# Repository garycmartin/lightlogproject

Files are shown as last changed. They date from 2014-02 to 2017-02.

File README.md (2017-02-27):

Lightlog Project
===============

A wearable, Open Source, ambient colour light tracker.

Installation
------------

To download data from Lightlog you'll need to set up your machine with some standard tools.

1) Install the device driver for the USB sync cable, install documentation steps, and driver are available at:

<http://www.picaxe.com/Software/Drivers/AXE027-USB-Cable-Driver/#download>

2) For Mac and Linux systems Python is usually already installed. If your using Windows and don’t have Python installed, there's a nice quick guide here if you need it. Please note that the scripts current require Python 2.7:

<http://www.anthonydebarros.com/2011/10/15/setting-up-python-in-windows-7/>

3) For Windows, make sure Python is added to your PATH variable, this is covered in the above guide.

```
C:\Python27;C:\Python27\Lib\site-packages\;C:\Python27\Scripts\;
```

4) Install pySerial module. The above guide also includes steps to add setuptools and pip, once you have them added you can type:

```shell
pip install pyserial
```

5) Download the lightlogdownload.py script from:

<https://raw.githubusercontent.com/garycmartin/lightlogproject/master/python/lightlogdownload.py>

…or make a local clone of the git repository. Github provides graphical git clients at <https://desktop.github.com> if needed.

6) Test that you can run the script ok by trying to use the command console or a shell window to check the script version:

```shell
python lightlogdownload.py --version
Version v0.13
```

7) Finally, plug in the serial cable, attach a Lightlog, and run the script...

Basic workflow
--------------

The usual work flow is to run:

```shell
python lightlogdownload.py --both
```

This will try to automatically find the connected serial port and communicate with Lightlog. Hold the button down on the Lightlog when it asks to establish the down link. The script will then download all logged data and save a .csv file of lux values containing red, green, blue, white, epoch seconds, and flags. The auto save file name includes the Light Log's unique ID, and if the save file already exists it will append any new data since the last download. This should make it easy to plug in each device, one after the other, and run the command each week to build up a continuous archive of data. Make sure you grab the data once a week (the default is one record a minute) or you'll have gaps in your data (at one record a minute, the memory holds 7days 14hrs worth of samples).

The epoch timestamps are seconds since 1st, Jan, 1970 (AKA Unix time, or POSIX time), you can quickly check a timestamp if needed with the below code snipped:

```shell
python -c 'import datetime; print (datetime.datetime(1970,1,1) + datetime.timedelta(seconds=1395802371))'
2014-03-26 02:52:51
```

For reference here's the download command's full arguments:

```
$ python lightlogdownload.py --help
usage: lightlogdownload.py [-h] [-p PORT] [-r] [-b] [--csv-header]
                           [--estimate]
                           [-f FILE | --stdout | --cal {2.5k,5k,10k} | --delay DELAY |
                           --phase PHASE | --sample SAMPLE | --status | --reset-memory |
                           --reset-cal | --reset-goal | --factory-reset | -v]
    
Download, convert and save data from Lightlog device. Without arguments data will be
saved to an auto-named csv file Light_Log_<device_ID>.csv in the current directory, if
the log file already exists, new data will be appended to the log.

optional arguments:
   -h, --help            show this help message and exit
   -p PORT, --port PORT  serial or COM port name
   -r, --raw             raw 10-bit sensor data, no conversion to lux scale
   -b, --both            auto saves two files, raw 10-bit sensor data and one
                         in lux
   --csv-header          outputs column header in first row of data (new log
                         files only)
   --estimate            force time estimate based on device period setting
                         rather than log time data
   -f FILE, --file FILE  save downloaded data to a named file
   --stdout              send data to console sandard output
   --cal {2.5k,5k,10k}   calibrate hardware to current lux light exposure
   --delay DELAY         fine tune device delay timing between samples 500-2000
                         (default 1000 = 10sec)
   --phase PHASE         set day phase 0-1439 in min (used for resetting daily
                         goal)
   --sample SAMPLE       number of samples per average 1-63 (default is 6
                         giving 1 record every minute)
   --status, -s          display device status data
   --reset-memory        reset memory pointer (for a fresh logging session)
   --reset-cal           reset lux calibration back to factory defaults
   --reset-goal          reset daily light goal
   --factory-reset       reset device back to all factory defaults, new unique
                         hardware ID will be generated (!!!)
   -v, --version         show download software version number and exit
```

Lightlogdownload.py script
--------------------------

When synching your devices I recommend using either the --raw or --both option, these generate a copy of the raw data before any calibration is applied (each device will generate a Light_Log_<device_ID>_raw.csv). If needed, this then allows you to control lux conversion/calibration using your own protocol, test equipment and math functions.

Without --raw or --both, you will only have the record of data after lux conversion has been applied using the code in Lightlogdownload.py. I have experimented with a number of fitted math curves to sample data sets, but none of them were satisfactory. My closest fit has been simply by interpolating between a set of lux vs. calibration data. The code is currently linearly interpolating between 16 calibration points.

Colour data
-----------

This python definition can be used if you want to convert the RGB values to colour temperature estimates:

```python
def calculate_colour_temp(colour):
   r = colour[0]
   g = colour[1]
   b = colour[2]
   n = ((0.23881 * r) + (0.25499 * g) + (-0.58291 * b)) / ((0.11109 * r) + (-0.85406 * g) + (0.52289 * b))
   cct = int(round(449 *  n ** 3 + 3525 *  n ** 2 + 6823.3 * n + 5520.33))
   return cct
```

Here’s another better commented example from Adafruit, where they use a library for the same sensor for Raspberry PI <https://github.com/adafruit/Adafruit-Raspberry-Pi-Python-Code/blob/master/Adafruit_TCS34725/Adafruit_TCS34725.py>

```python
def calculate_colour_temp2(colour):
   r = colour[0]
   g = colour[1]
   b = colour[2]

   # 1. Map RGB values to their XYZ counterparts.
   # Based on 6500K fluorescent, 3000K fluorescent
   # and 60W incandescent values for a wide range.
   X = (-0.14282 * r) + (1.54924 * g) + (-0.95641 * b)
   Y = (-0.32466 * r) + (1.57837 * g) + (-0.73191 * b) # also lux?
   Z = (-0.68202 * r) + (0.77073 * g) + ( 0.56332 * b)
    
   #2. Calculate the chromaticity co-ordinates
   xc = (X) / (X + Y + Z)
   yc = (Y) / (X + Y + Z)
    
   #3. Use McCamy's formula to determine the CCT
   n = (xc - 0.3320) / (0.1858 - yc)
    
   #Calculate the final CCT
   cct = (449.0 * n**3) + (3525.0 * n**2) + (6823.3 * n) + 5520.33
   return cct
```

For the raw data R, G, B, W, Time, Flag; R, G, B are 10-bit (0-1023) % of W, and W is a 10-bit exponential stored value of the original sensor reading (based on potentially two different 16-bit sensor gain exposures, depending on light brightness, see below).

The cases where you see W > R+G+B will be down to the 10-bit resolution the data is stored to memory. The sensor device samples 16-bit data, and may take two exposures of light (if needed) at different gains, one at x16, if that over exposes it then takes a second sample at x1 gain. It then takes the 16-bit W value and uses it to create a delta value for each R, G, B from W. W is then converted to 10-bits of data using a logarithmic scale so there is high detail for indoor lighting environments, but outdoor cases are still covered. R, G, B are then each converted to 10-bit (0-1023) % values of the W value (e.g. if the red sensor was 50% of the white sensor, R=511), this provides maximum resolution for R, G, B for both high values of W and low values of W.
 
The FIFO log buffer, with the default delay of one RGBW+flag record per minute, will last 7.5 days before data starts being ovberwritten. For the most accurate of log file timing it is best that some of your data overlaps your previous log, if found, lightlogdownload.py will use this data overlap to adjust sample deltas using the accurate system clock. If the data does not overlap lightlogdownload.py uses the devices sample rate to set a fixed time between records (most recent records will be the most accurate, with oldest records having most drift).
 
There are 64Kbytes available on the EEPROM for logging, each record is 6 bytes, giving 10922 available records 

You'll occasionally see something like this from lightlogdownload.py:

```
 Device day phase was 225min, now set to 227min
 Device delay tuning is set to 982 (984 suggested)
 ```
 
The first item refers to the day phase (1440min each day, local midnight=0min). The second appears if there was a reasonable number of new samples, it tells you the current timing delay used by this device, and its suggestion. You can see here it suggesting the device slows down a little to correct for the time drift. If you agree you can run:

```shell
$ python lightlogdownload.py --delay 984
```

It's not done automatically during a sync as it can't know how long you might have removed a battery for while replacing/changing. The delay value is already tuned at least a couple of times for the devices logging test data (over a couple of days duration minimum). Note that if your previous log file data overlaps with data in the device, lightlogdownload.py will adjust the sample timings between the start and end records using the real system time from your computer.

Battery life
------------

Expect 4 months (+/- a week) between battery changes under normal conditions. Be aware that very low temperatures will lower the battery voltage output.

If you want to have a safe margin of error, swap a battery once the script reports below 2.1V, you'll probably also notice the LEDs start to dim around this time as well.

The serial sync process and LED display are the most power hungry spikes that dip the voltage, so if the battery is low you may get a failed or no response message when trying to sync. Swapping out the battery for a new one, and trying to sync again should get all the data downloaded just fine.

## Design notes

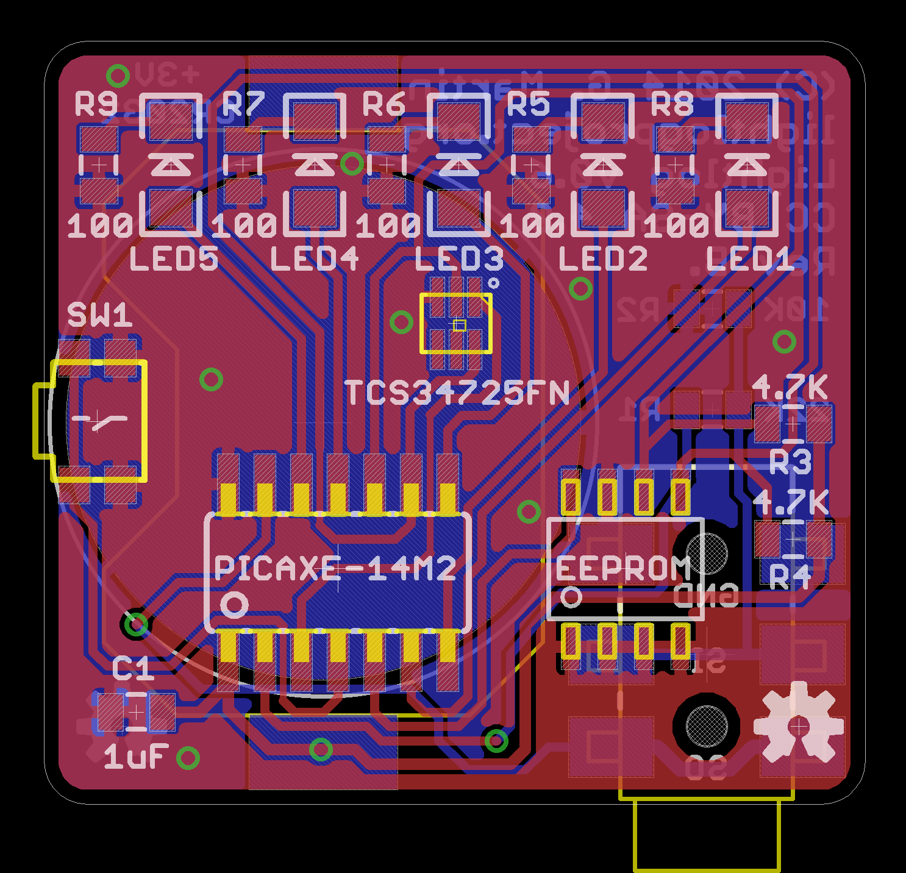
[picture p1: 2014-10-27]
circuit_design/LightLog_SMD_0.6B_BRD.png

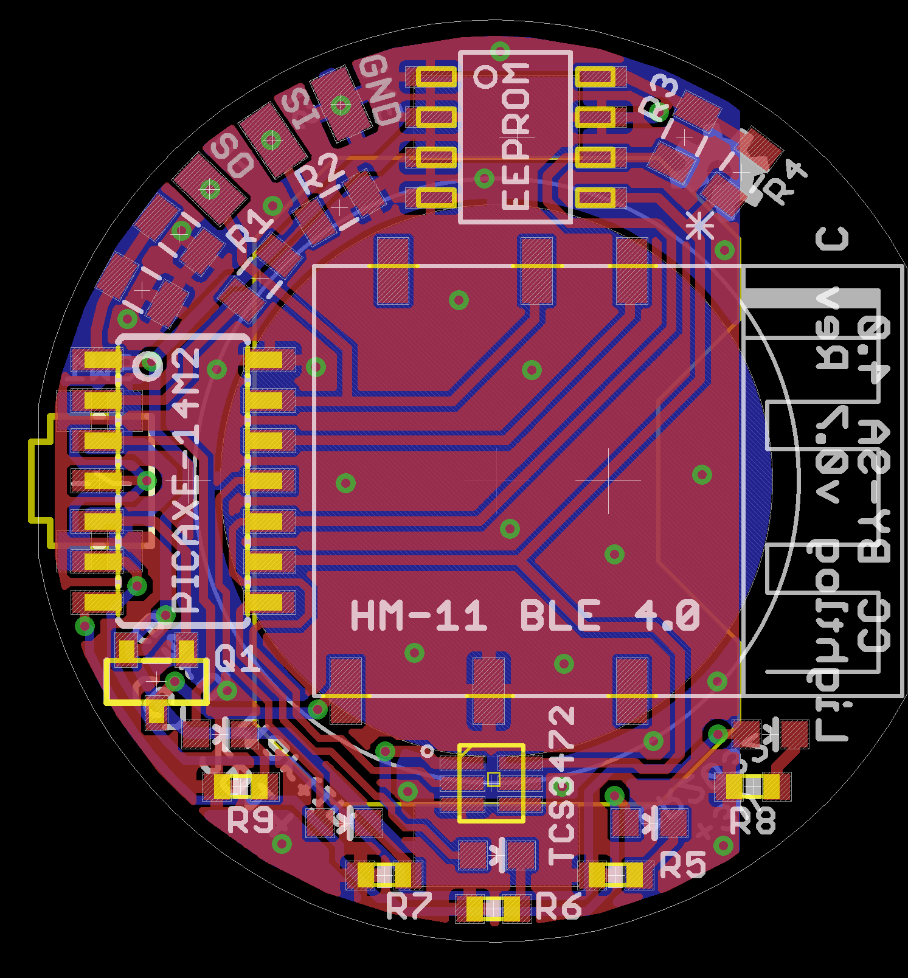
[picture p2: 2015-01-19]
circuit_design/LightLog_SMD_0.7_REV_C.png

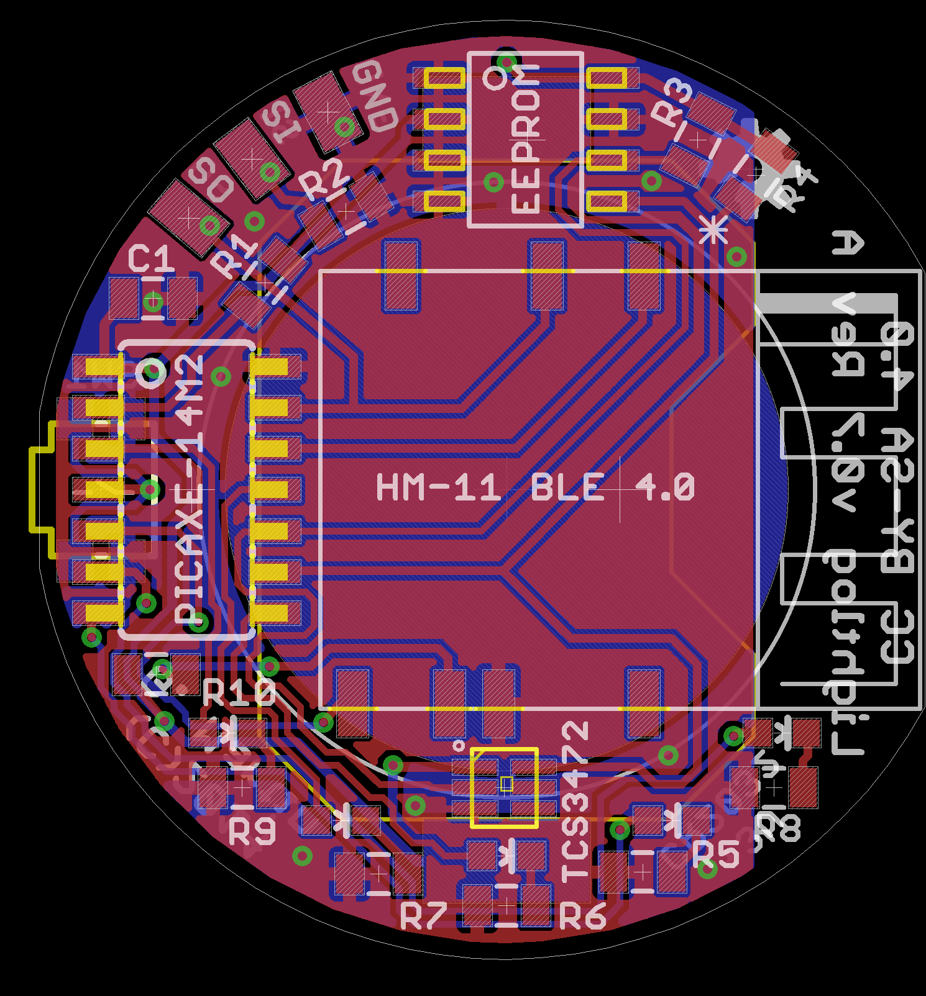
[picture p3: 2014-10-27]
circuit_design/LightLog_SMD_0.7_Rev_A.png

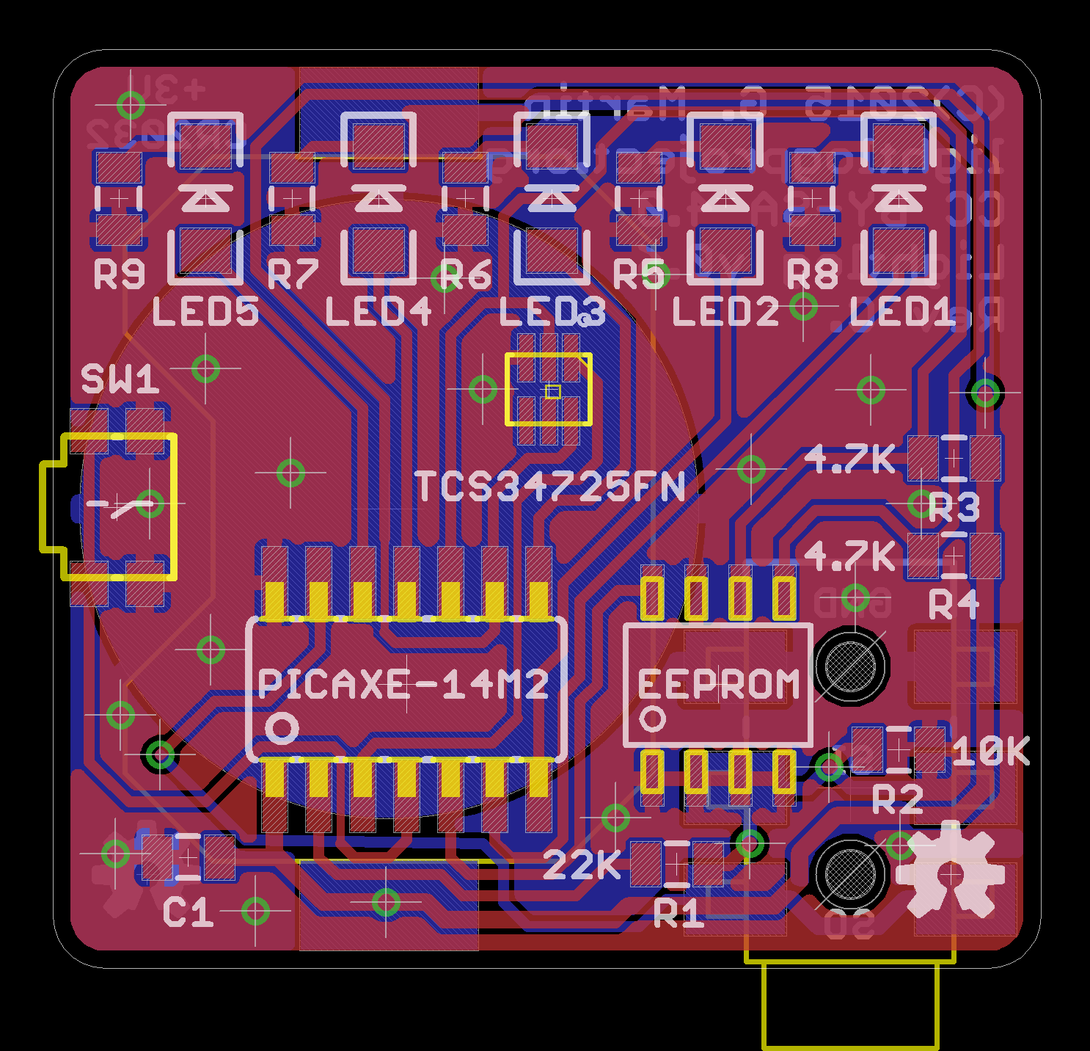
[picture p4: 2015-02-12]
circuit_design/LightLog_SMD_0.6_REV_C.png

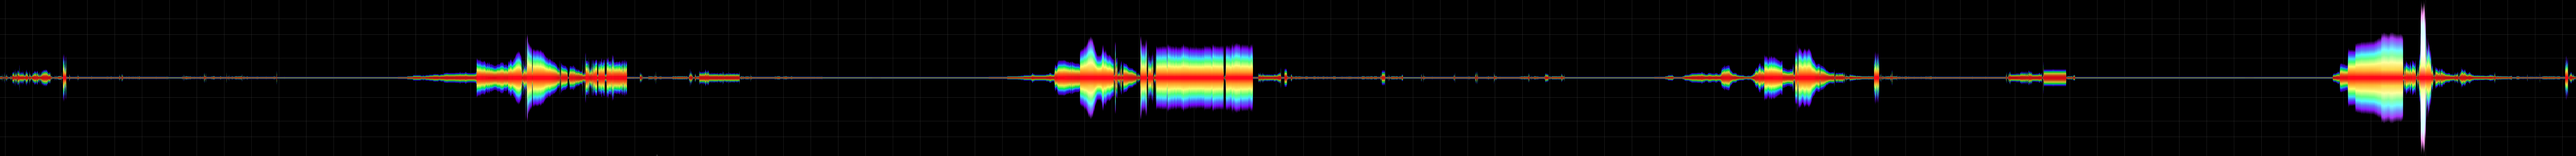
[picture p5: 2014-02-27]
data_log_samples/light_log_sample_data_2014-01-11-18-40-23_to_2014-01-15-20-29-13.png

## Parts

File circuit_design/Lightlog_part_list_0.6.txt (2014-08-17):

=== Light Log SMD/SMT prototype v0.6 part list ===

Surface Mount PICAXE-14M2 [AXE017M2SM]
24AA512-I/SN 64Kb Microchip EEPROM SMT slim SOIC-8 3.9mm width package (with extra low 1.7V drop-out)
TCS34725FN ams RGBC Light to Digital Converters (with IR filter)
C1. 100nF decoupling capacitor Y5V0805CTTE105Z Ceramic Capacitors MLCC - SMD/SMT
LED1, LED2, LED3, LED4, LED5 white VAOL-S12WR4 Standard LED - SMD
SMT Battery Holder BAT-HLD-001 Linx CR2032
R1 22Kohm SG73S2ATTD2202F KOA Speer Thick Film Resistors SMD (limit current to serial in)
R2 10Kohm SG73P2ATTD1002F KOA Speer Thick Film Resistors SMD (stops serial in from floating)
R3, R4 4.7Kohm SG73S2ATTD4701F KOA Speer Thick Film Resistors SMD (pull-ups for I2C)
R5, R6, R7, R8, R9 50ohm-100ohm SG73P2ATTD1000F KOA Speer Thick Film Resistors SMD (LED current limit)
SW1 Tactile side button SW04440 MICROSWITCH, MINIATURE; Actuation Type:S KMS231G LFS, C&K COMPONENTS
3.5mm stereo socket MJ4435-R SMD/SMT [CON039SM]
USB to 3.5mm jack FTDI based serial cable [AXE027] (for Pic serial programming and data sync)
CR2032 Coin cell battery 3V (circuit operating range 2.1V-5.5V, 240mAh will last >4 months)

Where given, part numbers [in square brackets] can be found at techsupplies.co.uk. Many parts can also be found at other suppliers such as mouser.com, cpc.farnell.com and farnell.com. This prototype requires a custom 2 layer PCB board, LightLog_SMD_0.6_BRD, for assembly due to small SMD/SMT components.

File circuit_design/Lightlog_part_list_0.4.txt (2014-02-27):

=== Light Log prototype v0.4 part list ===

PICAXE-14M2 [AXE017M2] (also available as a SMD component)
24LC512 64K EPROM [MIC051] (also available as a SMD component)
3 x Miniature LDR [SEN002] (~2Mohm dark current)
Red filter light gel (coloured acetate or cellophane will also work adequately)
Green filter light gel (coloured acetate or cellophane will also work adequately)
Blue filter light gel (coloured acetate or cellophane will also work adequately)
R3, R4, R5, R6, R7. 5 x 4.7Kohm resistors
C1. 100nF polyester decoupling capacitor (not strictly needed but recommended)
R8. 50ohm to 100ohm resistor (current limit for LED, can be omitted @ 3V or less operation)
LED (Example, diffused white 3mm LED 3.0-3.4V Forward Voltage, at 20mA from Adafruit)

USB to 3.5mm jack FTDI based serial cable [AXE027] (for Pic serial programming and light data sync)
3.5mm stereo socket [CON039] (or [CON039SM] for surface mount version)
R2. 10Kohm resistor to stop serial in from floating when disconnected from computer (essential for Pic operation)
R1. 22Kohm resistor to limit current in from computer to serial in

CR2032 Coin cell 3V (circuit will operate between 2.1V and 5.5V)
CR2032 battery holder (Example, [BAT004H] worked well dring breadboard prototyping)

Where given, part numbers (in square brackets) can be found at http://www.techsupplies.co.uk though many of these parts can be found at other suppliers.

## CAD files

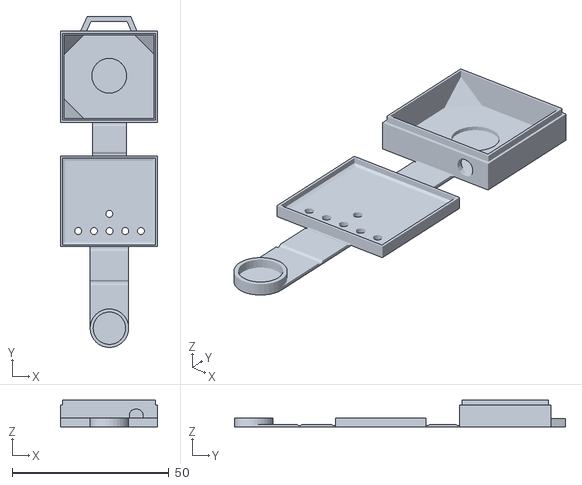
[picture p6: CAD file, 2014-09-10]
case_enclosures/LightLog_3d_enclosure.stl
30.8 x 105.5 x 8.55

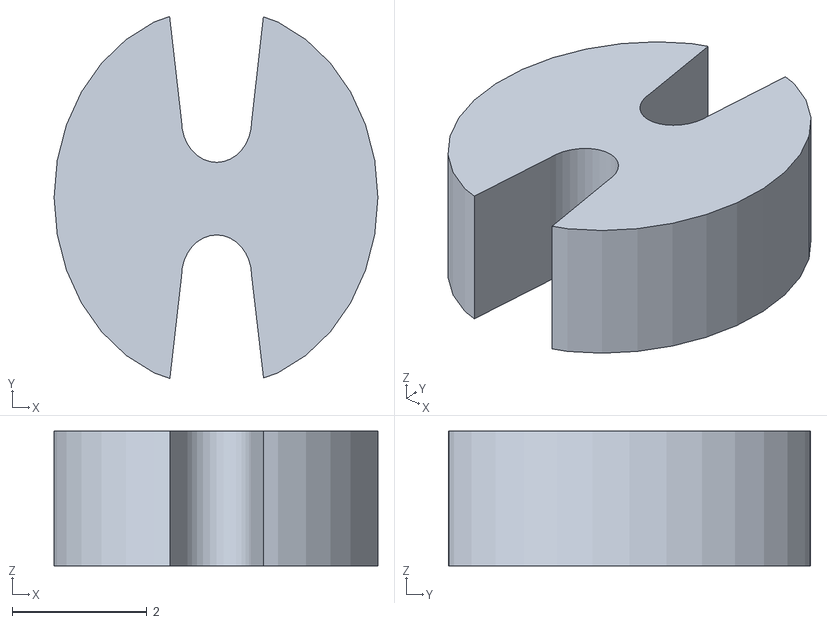
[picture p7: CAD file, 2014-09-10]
case_enclosures/LDR_spacer.stl
4.80 x 5.37 x 2.00

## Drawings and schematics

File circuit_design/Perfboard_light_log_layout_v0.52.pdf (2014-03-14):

Bottom copper view of main perfboard (v0.52) | Bottom copper view of power/comms perfboard (v0.52)

# Light Log Project (v0.52)

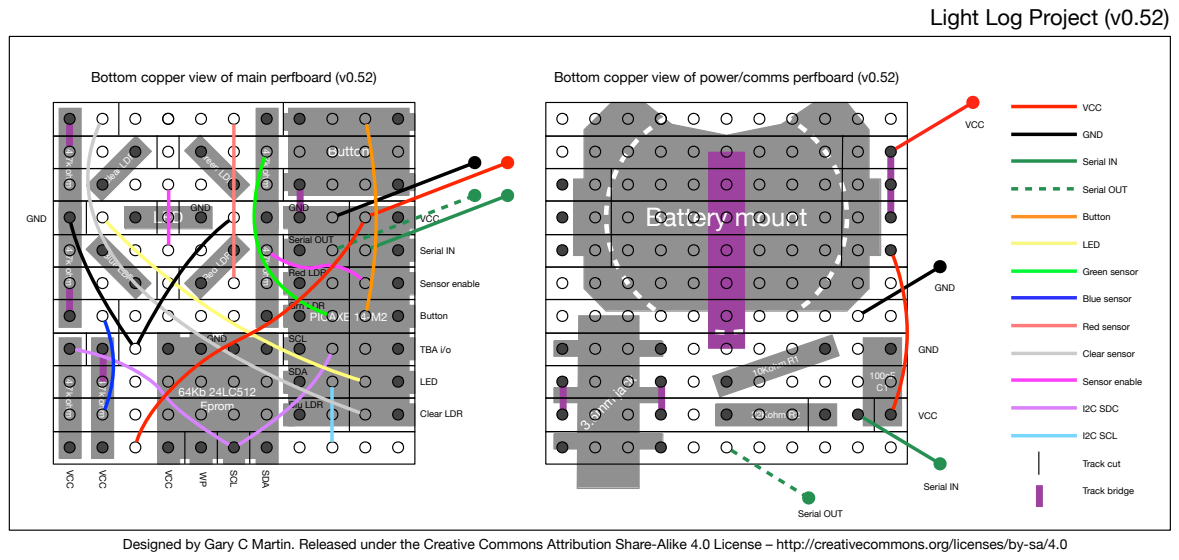
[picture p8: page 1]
PICAXE 14-M2; Button; 64Kb 24LC512 Eprom; 4.7k ohm; LED; Clear LDR; Red LDR; Green LDR; Blue LDR; 4.7k ohm 4.7k ohm; 3.5mm jack; 22Kohm R2; 10Kohm R1; Battery mount; TBA i/o; VCC; Serial IN; Sensor enable; SCL; SDA; GND; Serial OUT; Grn LDR; Blu LDR; Green sensor; Blue sensor; Red sensor; I2C SDC; I2C SCL; Clear sensor; Track cut; Track bridge

Designed by Gary C Martin. Released under the Creative Commons Attribution Share-Alike 4.0 License – http://creativecommons.org/licenses/by-sa/4.0

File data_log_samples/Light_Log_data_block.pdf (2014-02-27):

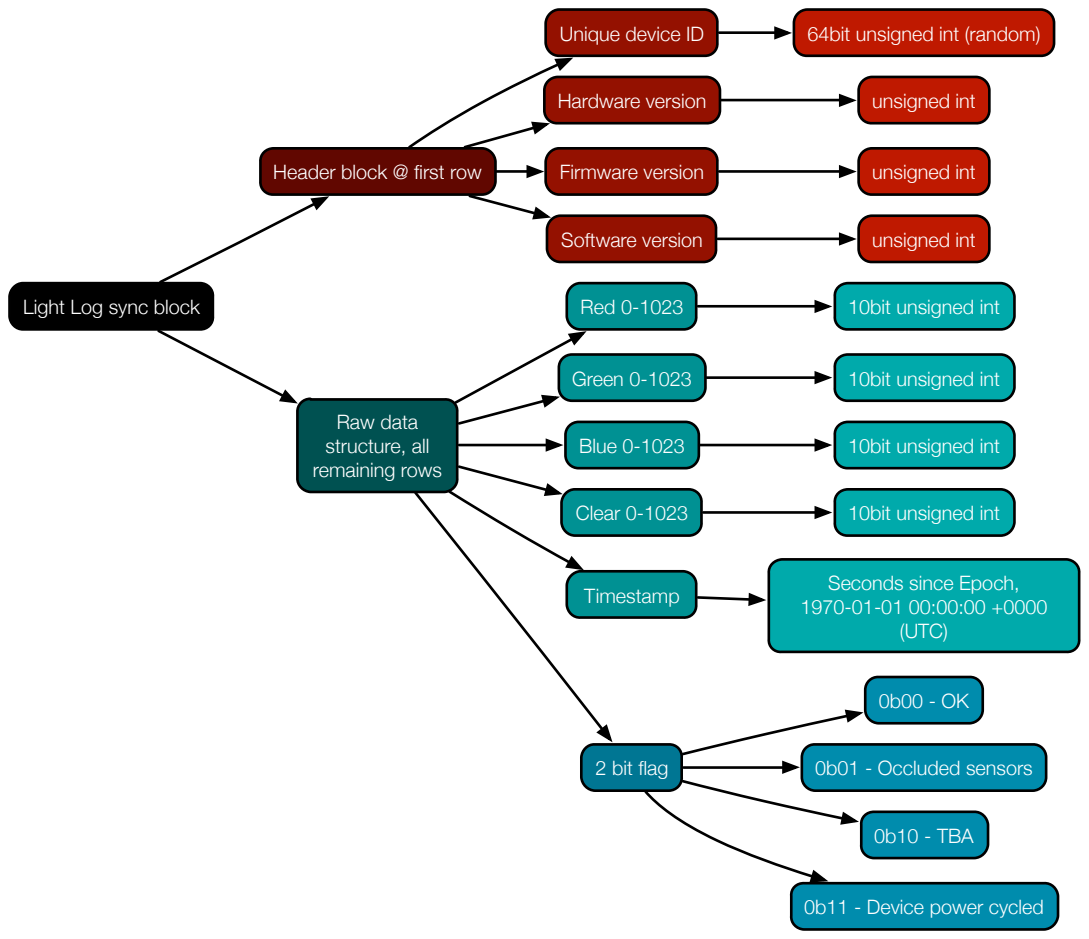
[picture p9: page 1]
Unique device ID; 64bit unsigned int (random); Hardware version; unsigned int; Firmware version; Software version; Raw data structure, all remaining rows; Red 0-1023; 10bit unsigned int; Green 0-1023; Blue 0-1023; Clear 0-1023; Timestamp; Seconds since Epoch,; 1970-01-01 00:00:00 +0000 (UTC); 2 bit flag; 0b01 - Occluded sensors; 0b10 - TBA

Header block @ first row

Light Log sync block

0b11 - Device power cycled

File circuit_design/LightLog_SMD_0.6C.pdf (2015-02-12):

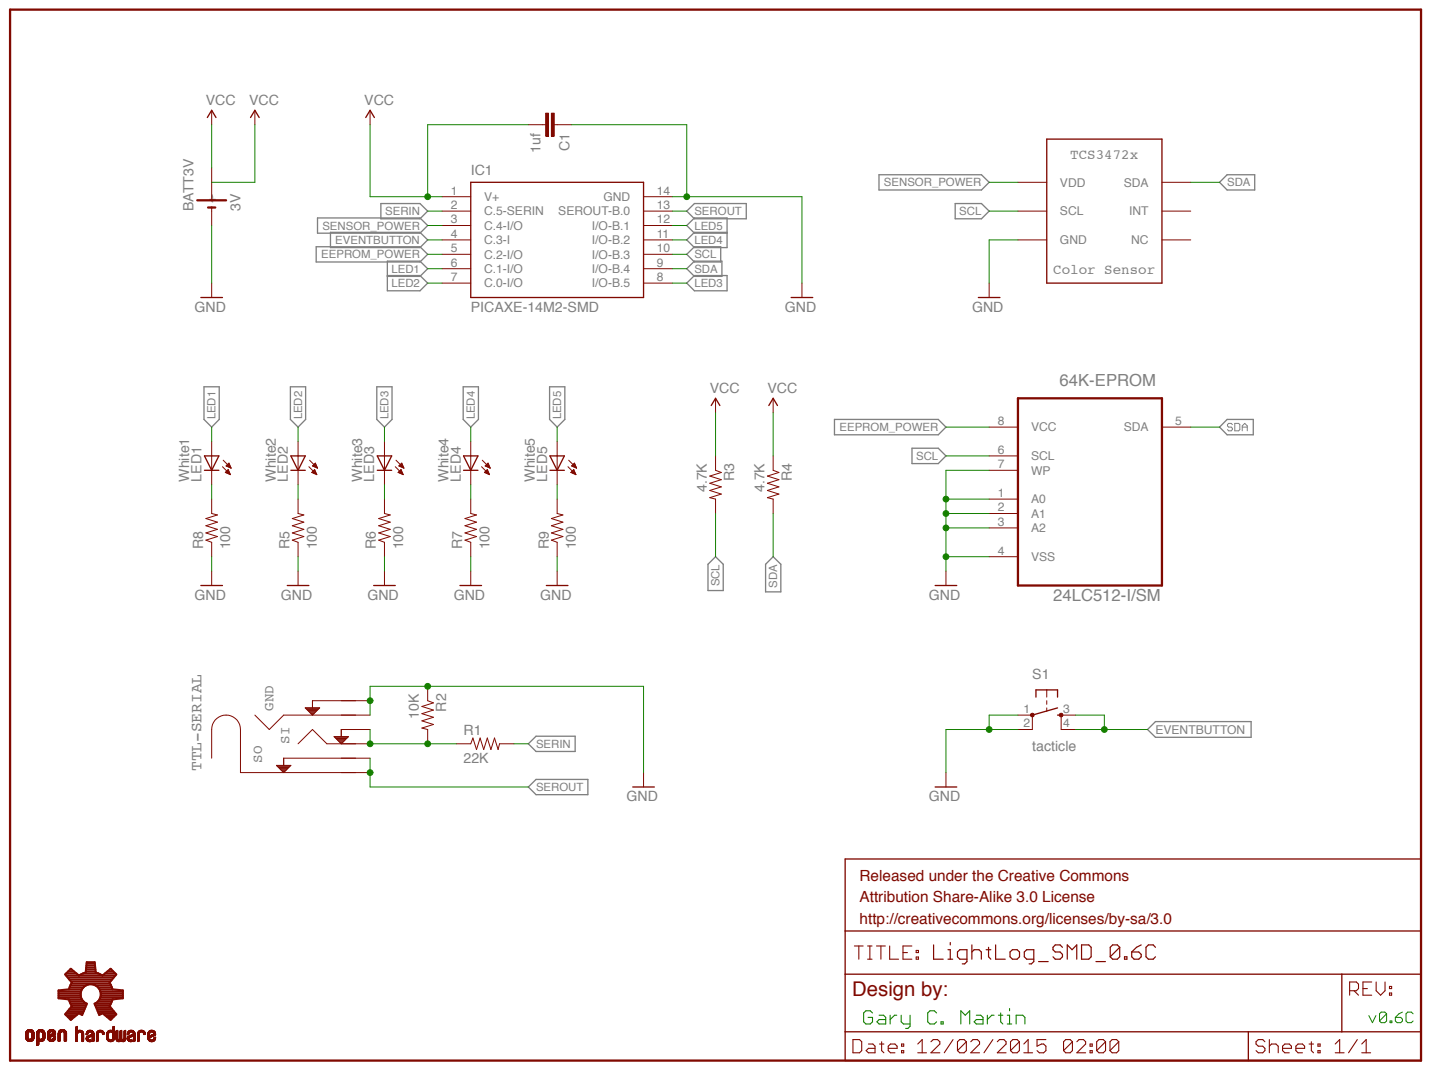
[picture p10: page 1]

Released under the Creative Commons
Attribution Share-Alike 3.0 License
http://creativecommons.org/licenses/by-sa/3.0

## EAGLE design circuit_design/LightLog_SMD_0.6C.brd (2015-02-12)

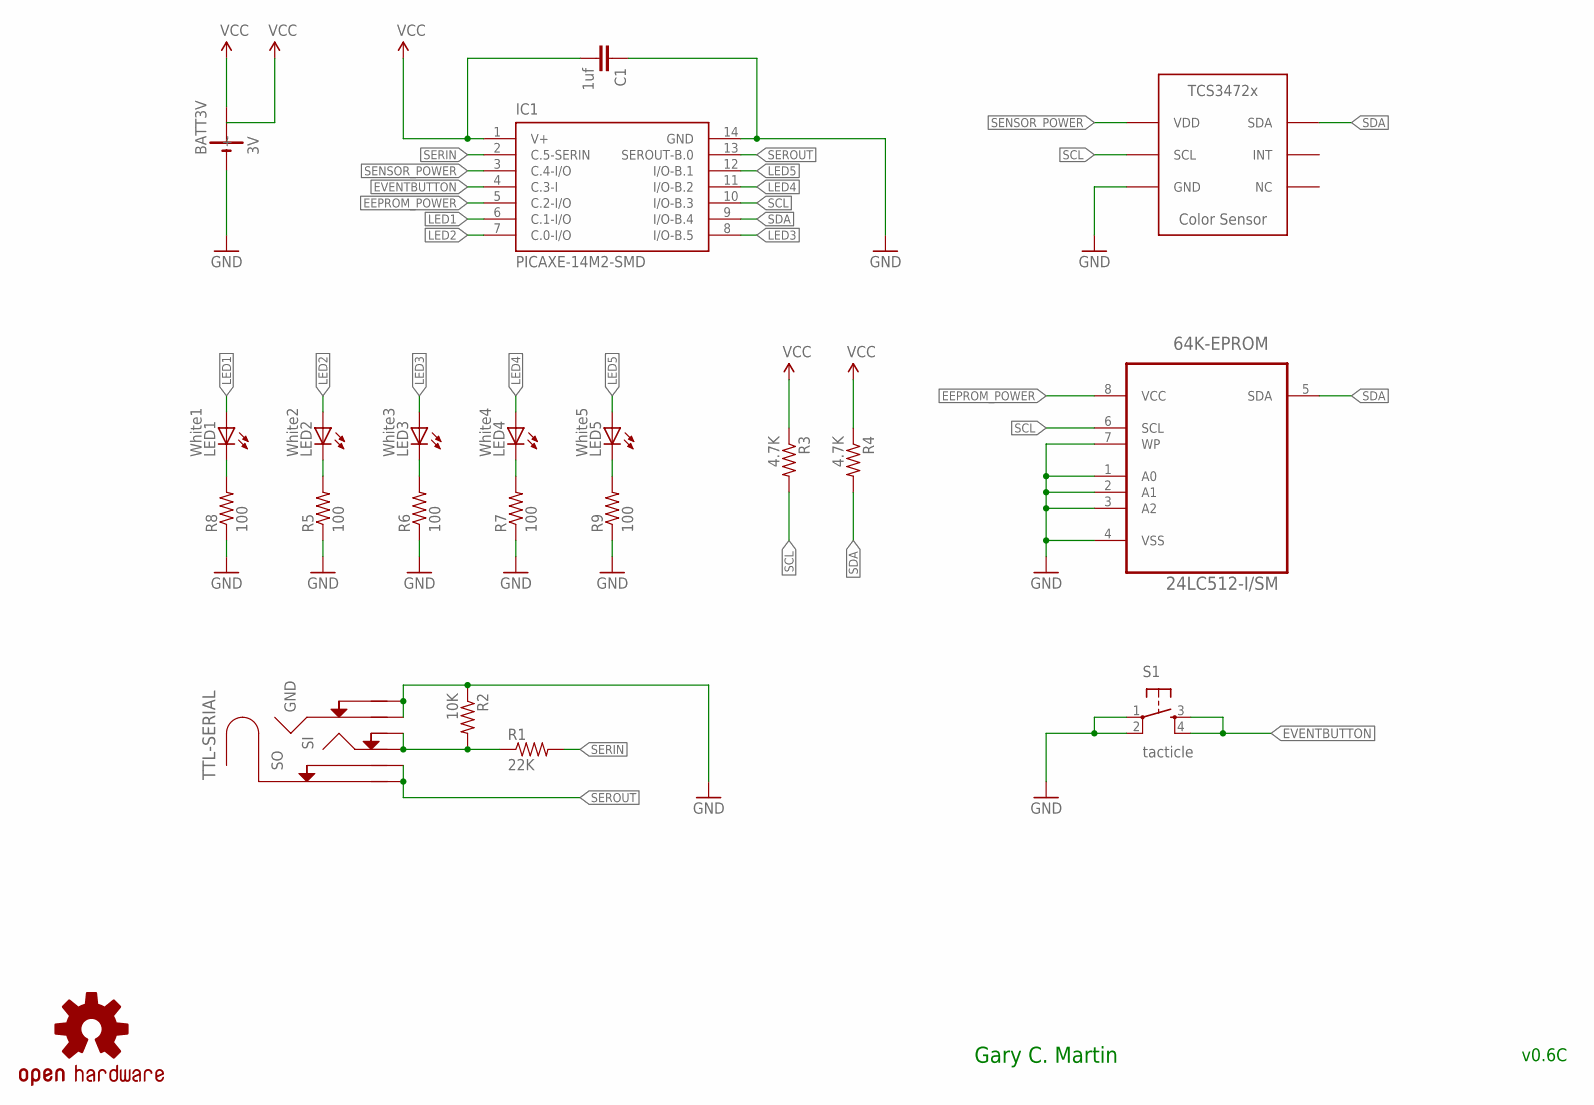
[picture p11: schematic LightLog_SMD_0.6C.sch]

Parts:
64K-EPROM: 24LC512-I/SM; SOIC127P794X203-8N
BATT3V: 3V; BAT-HLD-001-CR2032-SMD
C1: 1uf; 0805
IC1: PICAXE-14M2-SMD; SOIC14
LED1: White1; LED-1206
LED2: White2; LED-1206
LED3: White3; LED-1206
LED4: White4; LED-1206
LED5: White5; LED-1206
LOGO1: OSHW-LOGOS; OSHW-LOGO-S
R1: 22K; 0805
R2: 10K; 0805
R3, R4: 4.7K; 0805
R5, R6, R7, R8, R9: 100; 0805
S1: tacticle; TACTILE_SWITCH_SMD
TTL-SERIAL: 3-5MM-STEREO-SOCKET; 3-5MM-SMT
U$1: TCS3472; DUAL-FLAT-NO-LEAD-6PIN

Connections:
EEPROM_POWER: 64K-EPROM.8 (VCC), IC1.5 (C.2-I/O)
EVENTBUTTON: IC1.4 (C.3-I), S1.3, S1.4
GND: 64K-EPROM.1 (A0), 64K-EPROM.2 (A1), 64K-EPROM.3 (A2), 64K-EPROM.4 (VSS), 64K-EPROM.7 (WP), BATT3V.NEG (-), C1.1, IC1.14 (GND), R2.1, R5.1, R6.1, R7.1, R8.1, R9.1, S1.1, S1.2, TTL-SERIAL.5, TTL-SERIAL.6, U$1.3 (GND)
LED1: IC1.6 (C.1-I/O), LED1.A
LED2: IC1.7 (C.0-I/O), LED2.A
LED3: IC1.8 (I/O-B.5), LED3.A
LED4: IC1.11 (I/O-B.2), LED4.A
LED5: IC1.12 (I/O-B.1), LED5.A
unnamed: LED2.C, R5.2
unnamed: R1.1, R2.2, TTL-SERIAL.3, TTL-SERIAL.4
unnamed: LED3.C, R6.2
unnamed: LED4.C, R7.2
unnamed: LED5.C, R9.2
unnamed: LED1.C, R8.2
SCL: 64K-EPROM.6 (SCL), IC1.10 (I/O-B.3), R3.2, U$1.2 (SCL)
SDA: 64K-EPROM.5 (SDA), IC1.9 (I/O-B.4), R4.2, U$1.6 (SDA)
SENSOR_POWER: IC1.3 (C.4-I/O), U$1.1 (VDD)
SERIN: IC1.2 (C.5-SERIN), R1.2
SEROUT: IC1.13 (SEROUT-B.0), TTL-SERIAL.1, TTL-SERIAL.2
VCC: BATT3V.POS1 (+), BATT3V.POS2 (+), C1.2, IC1.1 (V+), R3.1, R4.1

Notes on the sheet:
Gary C. Martin
v0.6C

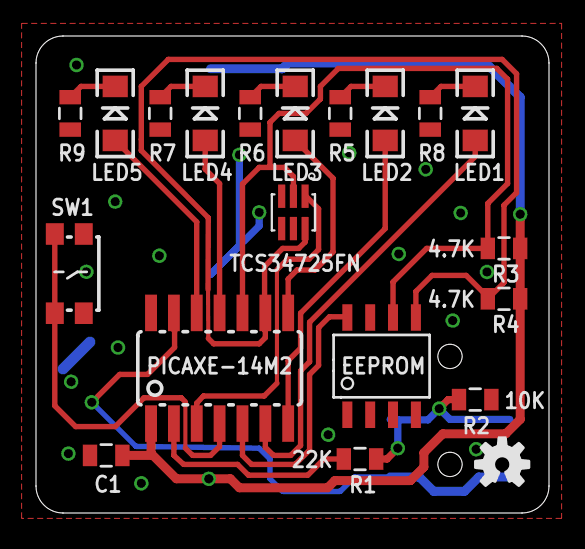
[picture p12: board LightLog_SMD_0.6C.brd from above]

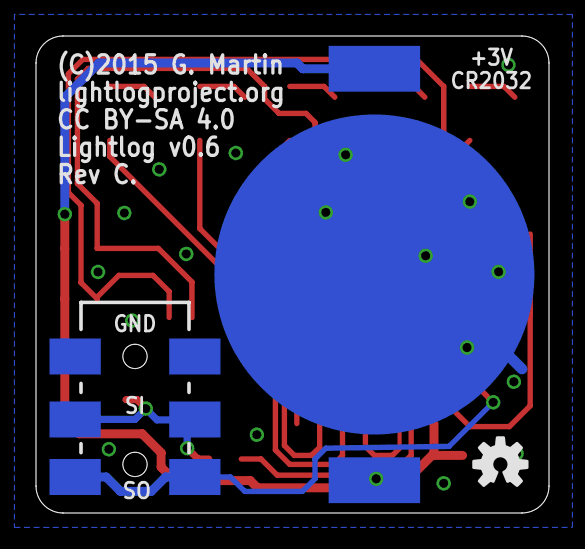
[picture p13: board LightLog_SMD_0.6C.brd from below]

Board: 2 copper layers, 28.5 x 26.5 mm, 23 parts (3 on the bottom side), 20 nets.

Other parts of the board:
LOGO2: OSHW-LOGOS; OSHW-LOGO-S

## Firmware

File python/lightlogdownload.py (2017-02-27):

#!/usr/local/bin/python
# coding=UTF-8
# Tested with Python 2.7
# Requires installation of the pyserial python module

# Copyright (c) 2013, 2014, Gary C. Martin <gary@lightlogproject.org>
# All rights reserved.
#
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
"""Download and convert data from a Lightlog <http://lightlogproject.org>.

Raw data bytes are downloaded from a Lightlog device through a serial port and
saved as a CSV file for easy processing with external tools. Time stamps use
calculations based on the local systems time, so be aware your local clock
should be reasonable accurate when downloading.
"""

import platform
import sys
import time
import math
import datetime
import argparse
import serial
from serial.tools import list_ports

#SERIAL_BAUD = 38400
SERIAL_BAUD = 19200
STEP_SECONDS = 60 # default grab from status 'Period' if available
VERSION = 'v0.13'


def limit(value, low, high):
    if value > high or value < low:
        raise argparse.ArgumentTypeError("value should be in range %d-%d" %(low, high))
    return value


def phase_limit(string):
    value = int(string)
    limit(value, 0, 1440)
    return value


def delay_limit(string):
    value = int(string)
    limit(value, 500, 2000)
    return value


def sample_limit(string):
    value = int(string)
    limit(value, 1, 64)
    return value


def get_args():
    """\
    Parse and return command line arguments.
    """
    parser = argparse.ArgumentParser(description='Download, convert and save data from Lightlog device. Without arguments data will be saved to an auto-named csv file Light_Log_<device_ID>.csv in the current directory, if the log file already exists, new data will be appended to the log.')

    parser.add_argument("-p", "--port",
                        help="serial or COM port name")
    parser.add_argument("-r", "--raw",
                        help="raw 10-bit sensor data, no conversion to lux scale",
                        action="store_true")
    parser.add_argument("-b", "--both",
                        help="auto saves two files, raw 10-bit sensor data and one in lux",
                        action="store_true")
    parser.add_argument("--csv-header",
                        help="outputs column header in first row of data (new log files only)",
                        action="store_true")
    parser.add_argument("--estimate",
                        help="force time estimate based on device period setting rather than log time data",
                        action="store_true")

    group = parser.add_mutually_exclusive_group()
    group.add_argument("-f", "--file",
                       help="save downloaded data to a named file")
    group.add_argument("--stdout",
                       help="send data to console sandard output",
                       action="store_true")
    group.add_argument("--cal",
                       help="calibrate hardware to current lux light exposure",
                       choices=['2.5k', '5k', '10k'])
    group.add_argument("--delay",
                       help="fine tune device delay timing between samples 500-2000 (default 1000 = 10sec)",
                       action="store",
                       type=delay_limit)
    group.add_argument("--phase",
                       help="set day phase 0-1439 in min (used for resetting daily goal)",
                       action="store",
                       type=phase_limit)
    group.add_argument("--sample",
                       help="number of samples per average 1-63 (default is 6 giving 1 record every minute)",
                       action="store",
                       type=sample_limit)
    group.add_argument("--status", "-s",
                       help="display device status data",
                       action="store_true")
    group.add_argument("--reset-memory",
                       help="reset memory pointer (for a fresh logging session)",
                       action="store_true")
    group.add_argument("--reset-cal",
                       help="reset lux calibration back to factory defaults",
                       action="store_true")
    group.add_argument("--reset-goal",
                       help="reset daily light goal",
                       action="store_true")
    group.add_argument("--factory-reset",
                       help="reset device back to all factory defaults, new unique hardware ID will be generated (!!!)",
                       action="store_true")
    group.add_argument("-v", "--version",
                       help="show download software version number and exit",
                       action="store_true")

    if parser.parse_args().version:
        print >> sys.stderr, "Version", VERSION
        sys.exit(0)

    return parser.parse_args()

def get_serial_ports():
    """\
    Return generator for available serial ports.
    """
    if platform.system() == 'Windows':
        # Windows
        for i in range(256):
            try:
                s = serial.Serial(i)
                s.close()
                yield 'COM' + str(i + 1)
            except serial.SerialException:
                pass
    else:
        # Unix
        for port in list_ports.comports():
            yield port[0]

def find_and_return_custom_cable():
    """\
    Search for a serial port matching the custom PICAXE cable name.
    """
    for p in serial.tools.list_ports.comports():
        if 'PICAXE' in p[1]:
            return p[0]
    return None

def parse_status_header(status):
    """\
    Extract data from Lightlog status header, returning a dictionary.
    """
    status_list = [i.split(':') for i in status.split(';')]
    status_dict = dict(zip([i[0] for i in status_list], [i[1] for i in status_list]))

    # Break out the individual R, G, B, and W values into a list
    status_dict['RGBW'] = map(int, status_dict['RGBW'].split(','))

    # Make a nice hex string of the two word unique ID
    status_dict['ID'] = '%0.4X%0.4X' % (int(status_dict['ID'].split(',')[0]),
                                        int(status_dict['ID'].split(',')[1]))

    # Battery output in mV
    if 'Batt' in status_dict:
        status_dict['Batt'] = int(status_dict['Batt'][:-2])

    if 'BattSlp' in status_dict:
        status_dict['BattSlp'] = int(status_dict['BattSlp'][:-2])

    if 'BattSen' in status_dict:
        status_dict['BattSen'] = int(status_dict['BattSen'][:-2])

    # Convert relavent strings to int
    for i in ('Goal', 'FW', '10KluxB', '5KluxB', '5KluxG', '5KluxR', '5KluxW', 'Delay',
              'Phase', '2.5KluxG','2.5KluxB','HW', '2.5KluxW','2.5KluxR', 'Period',
              '10KluxG', 'Boots', 'Wrap', '10KluxW', 'Pointer', '10KluxR', 'Batt',
              'BattSlp', 'BattSen'):
        if i in status_dict:
            status_dict[i] = int(status_dict[i])

    return status_dict

def convert_to_lux(red, green, blue, white, status_dict):
    """\
    Use pre-fitted average lux test data function to convert to lux.

    Ideally this function should use the current devices calibration data
    status_dict['2.5KluxW'], status_dict['5KluxW'], status_dict['10KluxW'],
    etc to convert sensor data to lux. Currently this function has been
    pre-fitted to average calibration data from multiple devices.
        RGB values are scaled relative to the clear sensor lux value as an
    estimate for how much each section of the spectra may map into the
    total lux value (lux is a measurement of the total visible spectrum EMF).
    RGB values are not (yet) calibrated to a set of known colour sources.
    """

    HW = status_dict['HW']
    r = float('%.4f' % linear_interpolation(red, HW))
    g = float('%.4f' % linear_interpolation(green, HW))
    b = float('%.4f' % linear_interpolation(blue, HW))
    w = float('%.4f' % linear_interpolation(white, HW))

    return r, g, b, w


def linear_interpolation(x, HW):
    """\
    Linear interpolation between recorded data point values from HW4 digital sensor devices.
    """
    if HW >= 5:
        # SMT digital sensor in white case with larger sensor window
        calibration_data = [(0, 0), (1, 39), (8, 193), (50, 389), (100, 461), (250, 521), (500, 605), (1000, 673), (2500, 762), (5000, 819), (10000, 854), (15000, 880), (33000, 983), (60000, 1023)]

    elif HW == 4:
        # SMT digital sensor
        calibration_data = [(0, 0), (1, 29), (8, 175), (20, 258), (40, 321), (140, 446), (500, 572), (1000, 632), (1500, 658), (2000, 716), (2500, 0x322), (5000, 0x35F), (10000, 0x3A2), (20000, 945), (27000, 953), (85000, 0x3FF)]
        
    else:
        # LDR prototypes
        calibration_data =  [(0,0), (1, 28), (10, 60), (50, 213), (100, 296), (200, 406), (300, 461), (500, 531), (1000, 633), (2500, 794), (5000, 838), (10000, 862), (20000, 887), (54000, 902), (58000, 903), (60000, 904), (66000, 905), (80000, 908), (85000, 909), (116000, 917), (200000, 1023)]

    calibration_data.reverse()
    x = float(x)
    result = None
    old_pair = None
    for pair in calibration_data:
        if x >= pair[1] and old_pair:
            result = (x - pair[1]) / (old_pair[1] - pair[1]) * (old_pair[0] - pair[0]) + pair[0]
            break
        old_pair = pair

    return result
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

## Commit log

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2013-10-19 Power, sampling, serial comms & flag changes.
    Improved avarages (no roll over between saved samples, more accurate)
    Added dump data and continue test routine
    Added serial cmd commands
    Dropped to 2Mhz = serial 2400bps (any slower seems to make serial io flakey)
    Replaced 255,255,255,255 reboot with extra_byte 2-bit flag in data
    High speed erase (should do this for data sync next)
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2014-02-27 Example data block format from a Light Log sync
    [light_log_sample_data_2014-01-11-18-40-23_to_2014-01-15-20-29-13.csv]
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2014-03-08 Fix symbol reference for button input pin
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2014-03-24 Use correct exit code for comms fail case.
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2014-03-27 Corrected name for clear LDR sensor.
2014-03-27 Corrected push button switch to be down to GND.
    Micro controller supports internal pull up resistors, not pull down
    resistors.
2014-03-28 Changed from 15 to 6 samples per min with more sleeping.
    This saving more power, and seems to avoid an occasional device reboot
    (theory is due to using many short naps to make the previous 2sec
    sleep). Using a mix of 1.1sec, 3 x 2.2sec, and 2.3sec for a total of
    10seconds of low power.
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2014-08-17 Fix intermittent I2C write issue
    Write to I2C one byte at a time to prevent intermittent case where two
    bytes could be swapped.
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2014-08-27 Don't fail if header is missing some stat
    Header stat data can be prone to change from time to time so don’t bail
    unless some critical data is missing.
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2014-09-10 Eagle CAD board and schematic for SMT v0.6
    [LightLog_SMD_0.6.brd, LightLog_SMD_0.6.sch]
2014-09-10 Eagle CAD board and schematic for SMT v0.6B
    Revision B has some minor label corrections and larger drill holes for
    the 3.5 SMT jack socket component.
    [LightLog_SMD_0.6B.brd, LightLog_SMD_0.6B.sch]
2014-09-10 Initial enclosure work
    Blocking out volume needed for hand build prototype
    [LightLog_3d_enclosure.stl]
2014-09-10 Adding more detail to device volume
    [LightLog_3d_enclosure.stl]
2014-09-10 Revert "Adding more detail to device volume"
    This reverts commit 9381a92e6241ea29a37aab7485646c7582f03154.
    [LightLog_3d_enclosure.stl]
2014-09-10 Revert 9381a92..73068e1
    This rolls back to commit 9381a92e6241ea29a37aab7485646c7582f03154.
    [LightLog_3d_enclosure.stl]
2014-09-10 Revert 063dc00..d9de705
    This rolls back to commit 063dc00caafd59538c64db55e60c1f2b3c843db0.
    [LightLog_3d_enclosure.stl]
2014-09-10 Wrong branch...
    [LightLog_3d_enclosure.stl]
2014-09-10 Initial commit blocking out device case volume
    [LightLog_3d_enclosure.stl]
2014-09-10 Adding detail to volume
    [LightLog_3d_enclosure.stl]
2014-09-10 Circular case with clip
    [LightLog_3d_enclosure.stl]
2014-09-10 Clip and inside changes
    [LightLog_3d_enclosure.stl]
2014-09-10 New fitted square case
    [LightLog_3d_enclosure.stl]
2014-09-10 Replace clip with hair grip like fastener
    [LightLog_3d_enclosure.stl]
2014-09-10 Rounded clip fastener edges
    Corners were rather scratchy to wear
    [LightLog_3d_enclosure.stl]
2014-09-10 New higher res internal volume shape
    [LightLog_3d_enclosure.stl]
2014-09-10 Slip case design for flexible PLA
    Bendy case with front and back cover parts, magnet used for fastening.
    [LightLog_3d_enclosure.stl]
2014-09-10 Added slot for fastener
    [LightLog_3d_enclosure.stl]
2014-09-10 Slot size reduction
    [LightLog_3d_enclosure.stl]
2014-09-10 Rounded sensor window with extruded rim
    [LightLog_3d_enclosure.stl]
2014-09-10 Added round window for LED location
    [LightLog_3d_enclosure.stl]
2014-09-10 More size tweaks
    [LightLog_3d_enclosure.stl]
2014-09-10 More small size tweaks
    [LightLog_3d_enclosure.stl]
2014-09-10 Removed circle from strap and padded battery fit
    [LightLog_3d_enclosure.stl]
2014-09-10 More battery empty volume filling
    [LightLog_3d_enclosure.stl]
2014-09-10 Solid case without magnetic strap
    Two separate sections for ridged XT material, separate badge clip can
    be used to attach
    [LightLog_3d_enclosure.stl]
2014-09-10 New device diamond ridged enclosure
    New prototype with sensors in a 2x2 grid (RGB and clear). ridged two
    part case with attachment for separate badge clip.
    [LightLog_3d_enclosure.stl]
2014-09-10 Clip fastening improvements
    [LightLog_3d_enclosure.stl]
2014-09-10 Case 43
    [LightLog_3d_enclosure.stl]
2014-09-10 Case 46
    [LightLog_3d_enclosure.stl]
2014-09-10 Case 48
    [LightLog_3d_enclosure.stl]
2014-09-10 Case 52
    [LightLog_3d_enclosure.stl]
2014-09-10 Case 53
    [LightLog_3d_enclosure.stl]
2014-09-10 Case 54
    [LightLog_3d_enclosure.stl]
2014-09-10 Case 56
    [LightLog_3d_enclosure.stl]
2014-09-10 Case 59
    [LightLog_3d_enclosure.stl]
2014-09-10 Case 60
    [LightLog_3d_enclosure.stl]
2014-09-10 Case 61
    [LightLog_3d_enclosure.stl]
2014-09-10 Case 62
    [LightLog_3d_enclosure.stl]
2014-09-10 Case 65
    [LightLog_3d_enclosure.stl]
2014-09-10 Case 67
    [LightLog_3d_enclosure.stl]
2014-09-10 Case 69
    [LightLog_3d_enclosure.stl]
2014-09-10 Case 72
    [LightLog_3d_enclosure.stl]
2014-09-10 Case 74
    [LightLog_3d_enclosure.stl]
2014-09-10 Case 75
    [LightLog_3d_enclosure.stl]
2014-09-10 Case 77
    [LightLog_3d_enclosure.stl]
2014-09-10 Case 78
    [LightLog_3d_enclosure.stl]
2014-09-10 Spacer for LDR component
    Spacer to go behind hand soldered LRD sensors to position them close to
    the case sensor ‘window’ for maximum exposure.
    [LDR_spacer.stl]
2014-09-10 Case 85
    [LightLog_3d_enclosure.stl]
2014-09-10 Case 87
    [LightLog_3d_enclosure.stl]
2014-09-10 Case 89
    [LightLog_3d_enclosure.stl]
2014-09-10 Case 91
    Switching to two part soft case with magnetic strap, square rather than
    diamond orientation
    [LightLog_3d_enclosure.stl]
2014-09-10 Case 93
    Soft, flexible all in one case
    [LightLog_3d_enclosure.stl]
2014-09-10 Case 95
    [LightLog_3d_enclosure.stl]
2014-09-10 Case 100
    [LightLog_3d_enclosure.stl]
2014-09-10 Case 104
    [LightLog_3d_enclosure.stl]
2014-09-10 Case 111
    [LightLog_3d_enclosure.stl]
2014-09-10 Case 113
    [LightLog_3d_enclosure.stl]
2014-09-10 Case 116
    [LightLog_3d_enclosure.stl]
2014-09-10 Case 118
    [LightLog_3d_enclosure.stl]
2014-09-10 Case 119
    [LightLog_3d_enclosure.stl]
2014-09-10 Case 120
    [LightLog_3d_enclosure.stl]
2014-09-10 Case 123
    [LightLog_3d_enclosure.stl]
2014-09-10 Case 125
    [LightLog_3d_enclosure.stl]
2014-09-10 Case 130
    [LightLog_3d_enclosure.stl]
2014-09-10 Case 131
    [LightLog_3d_enclosure.stl]
2014-09-10 Case 135
    [LightLog_3d_enclosure.stl]
2014-09-10 Case 142
    [LightLog_3d_enclosure.stl]
2014-09-10 Case 147
    [LightLog_3d_enclosure.stl]
2014-09-10 Case 149
    [LightLog_3d_enclosure.stl]
2014-09-10 Case 151
    [LightLog_3d_enclosure.stl]
2014-09-10 Case 154
    [LightLog_3d_enclosure.stl]
2014-09-10 Case 157 for new SMT board
    First version of thin, single part case for the custom SMT board.
    [LightLog_3d_enclosure.stl]
2014-09-10 Case 159
    [LightLog_3d_enclosure.stl]
2014-09-10 Case 160
    [LightLog_3d_enclosure.stl]
2014-09-10 Case 161
    [LightLog_3d_enclosure.stl]
2014-09-10 Case 162
    [LightLog_3d_enclosure.stl]
2014-09-10 Channel data scaled to better fill 10 bit range
    Data is now scaled to better fit the 10bit space (previously was 1/16
    short of 0x1111111111 max). Refactor of bit_compress procedures to save
    some memory and make code cleaner. Lux calibration updated to match new
    scale.
2014-09-15 Compress code bug fix for first stage
    Mixup with and/or for the lowest level of light in x16 gain mode
    leading to a +64 offset in the data set for the minimal range of light
    levels.
2014-09-15 Fix bug introduced in daily light goal logic
    Program flow changes were going through test that were previously
    avoided after clobbering tmp2_word with some other work value causing
    goal to be indicated as reached incorrectly.
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2014-10-06 New BLE SMT board (version 0.7 revision A)
    New hardware required some changes to micro-controller pin outs so will
    require updated and different firmware branch.
    [LightLog_SMD_0.7.brd, LightLog_SMD_0.7.sch]
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2014-12-24 New SMD 0.7B board revision files
    Removes unnecessary pull-up resistor for BLE reset pin; adds P-Type
    MOSFET to provide enough current for BLE on power spike from a micro
    output pin; wider traces where possible; LED outputs nudged down a
    little; more GND vias
    [LightLog_SMD_0.7B.brd, LightLog_SMD_0.7B.sch]
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2015-02-12 Lightlog v0.6 REV C board
    Small changes to improve ease of reflow and applying solder paste
    stencil masking, only two components need to be hand soldered to the
    back of the board (battery holder and data sync socket).
    [LightLog_SMD_0.6C.brd, LightLog_SMD_0.6C.sch]
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2015-03-10 Bug fix, make sure delay status value from device is converted to an int.
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

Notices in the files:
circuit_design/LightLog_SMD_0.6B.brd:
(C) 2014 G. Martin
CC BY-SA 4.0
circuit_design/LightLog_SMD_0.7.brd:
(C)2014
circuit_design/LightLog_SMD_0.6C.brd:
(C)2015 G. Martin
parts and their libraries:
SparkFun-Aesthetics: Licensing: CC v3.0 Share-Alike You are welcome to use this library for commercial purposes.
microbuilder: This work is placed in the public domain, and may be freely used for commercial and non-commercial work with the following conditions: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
